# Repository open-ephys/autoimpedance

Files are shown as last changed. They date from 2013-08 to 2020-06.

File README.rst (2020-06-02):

**Warning** This project is deprecated! If you have interest in creating an open source automated electrode plater, please get in touch with us!

=====================
Autoimpedance
=====================

In neuroscience studies, it's important to measure electrode impedances before every experiment. If impedance levels are not in the right range, they must be adjusted by plating electrode tips with gold or platinum. The most common way to do this is with an analog impedance meter and current source, but this method is slow and unreliable. Autoimpedance will be an open-source, digital alternative that aims to speed up the impedance measurement and plating process.

This repository contains code, schematics, and board designs for Autoimpedance. It's based on the Electric Imp and the Analog Devices AD5933_ impedance converter.

Most of the code has been written for Arduino_, but it will soon be translated into Squirrel. PCB layout was done with Eagle_.

What's been done so far
-----------------------------------
- board layout with 32-channel multiplexing capabilities, with the ability to toggle between impedance testing (Analog Devices AD5933) and an adjustable current source (LM234).
- assemble prototype board and verify that multiplexing is working (multiplexing.pde_)
- write code for I2C communication with AD5933 and AD5245 programmable potentiometer (autoimpedance.pde_)

TODO List (short term)
-------------------------------
- calibrate the AD5933 (see instructions in the datasheet_)
- calibrate the LM234 adjustable current source
- create a simple webpage to manually control the device via WiFi
- write and refine a simple feedback algorithm to automatically bring impedance to desired levels
- design and manufacture a case

.. _AD5933: http://www.analog.com/en/rfif-components/direct-digital-synthesis-dds/ad5933/products/product.html
.. _Arduino: http://www.arduino.cc/
.. _Eagle: http://www.cadsoftusa.com/
.. _datasheet: https://github.com/open-ephys/autoimpedance/blob/master/PCB/AD5933.pdf
.. _autoimpedance.pde: https://github.com/open-ephys/autoimpedance/blob/master/autoimpedance.pde
.. _multiplexing.pde: https://github.com/open-ephys/autoimpedance/blob/master/multiplexing.pde

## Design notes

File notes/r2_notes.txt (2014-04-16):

Potential autoimpedance circuit improvements

1. There should be some extra, auxiliary MUX paths tied to various onboard dummy loads (e.g. 10k, 100k, 1M) for gain-factor calibration verification and internal phase measurements (see pgs. 17-19 of AD5933 datasheet).

2. There should be more test points on the circuit.

	> For testing digital pot resistance
	> Power rails
	> I2C bus sockets

3. There should be more information on the silkscreen layers - i.e. component values. 

4. Silk screen font must be larger because print resolution is too course for current size.

X5. Do we need a DC blocking cap at the test_out pin of the AD5933 to prevent the DC bias (table 5 of AD5933 datasheet) on test signal from electroplating during the impedance test?

	> EDIT 1: The DC offset is almost certainly a result of the single supply nature of the ic. The best way to fix this might be to implement a simple virtual ground circuit, and a higher voltage battery to create a negative rail. Then the test signal could be level shifted to 0V. Of course, vgnd would need to drive the saline bath too, so it would have to be a least a little hefty. We could also just send the test signal though an isolator although I doubt Josh will like that approach.
	
	> EDIT 2: The input stage of the AD5933 uses VDD/2 as a reference. Thus, all signals coming out of the device are referenced to this virtual ground, causing them to effectively be bipolar from the perspective of the electrode. Therefore, no DC blocking should be required.

X6. What p2p excitation voltage should we be using?

	> EDIT: Something around 100-200mVPP

X7. Why is the external oscillator required?

	> EDIT: Because the dynamic range with onboard oscillator is 1kHz to 100 kHz, and it is not really accurate in the low end where we need it.

8. There needs to be an off, or at least, reset switch. Sometimes AD5933 becomes unresponsive and requires a power cycle to get back to normal. This could be a programming error, but its good to have a fail-safe.

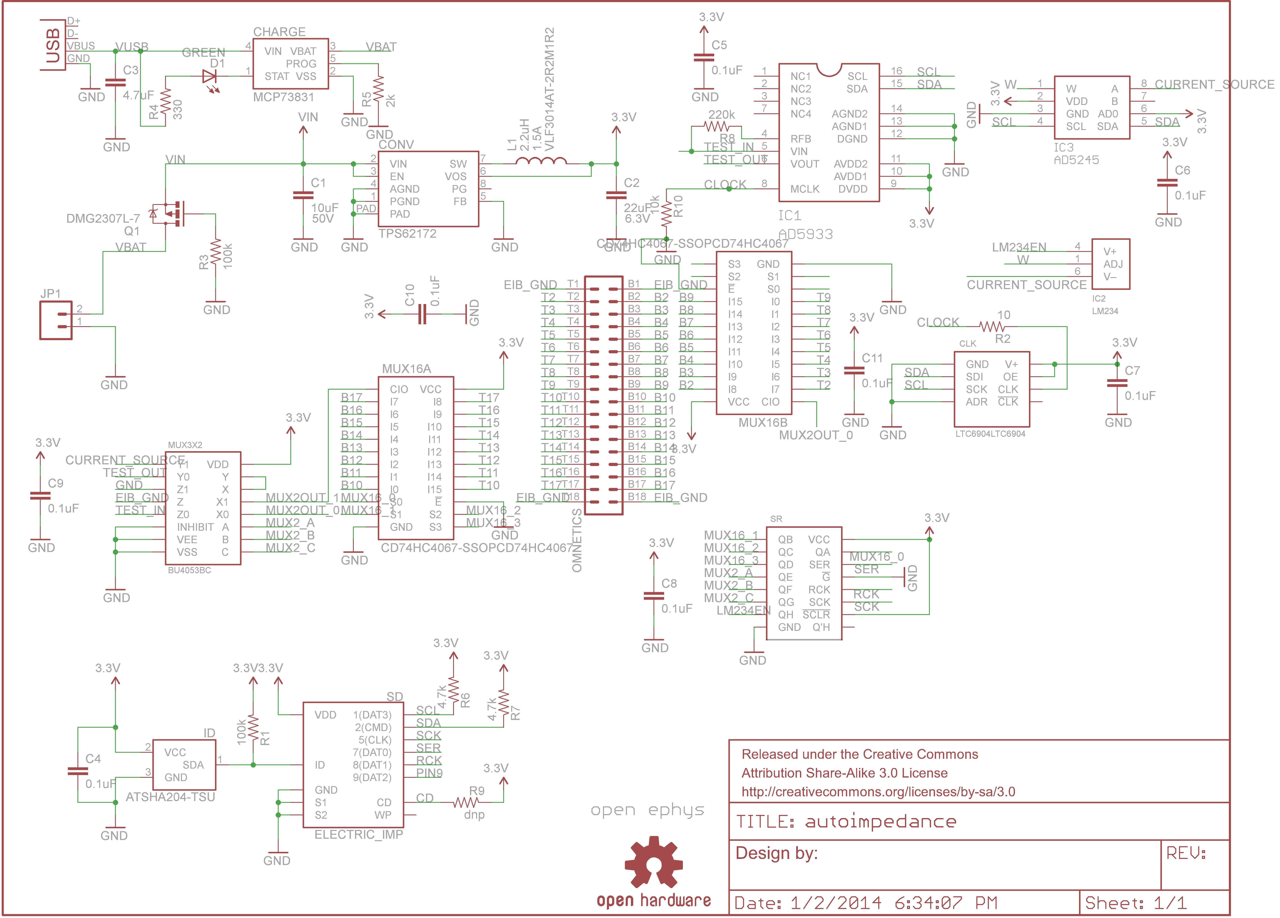
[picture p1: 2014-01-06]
Images/autoimpedance.sch.png

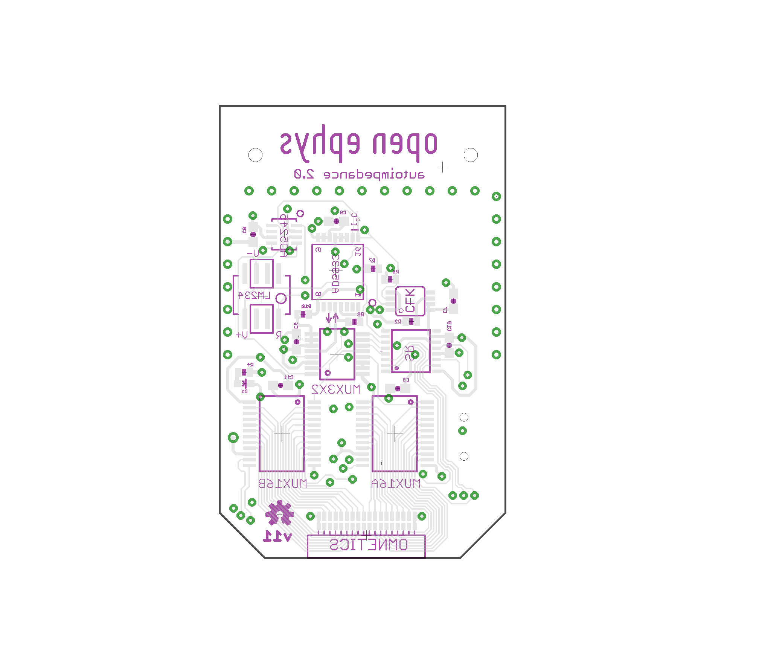
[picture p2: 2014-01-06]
Images/autoimpedance.brd.png

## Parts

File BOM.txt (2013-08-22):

https://docs.google.com/spreadsheet/ccc?key=0An1VoeoG8K6AdDJwWjhla1g5R3o2WVY2MWo2YUxCS2c&usp=sharing

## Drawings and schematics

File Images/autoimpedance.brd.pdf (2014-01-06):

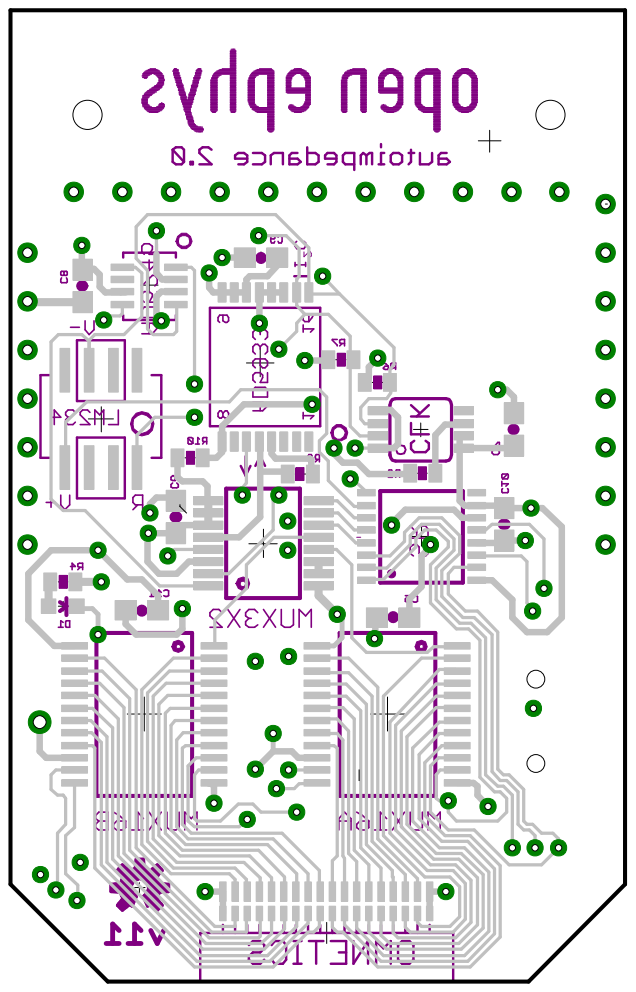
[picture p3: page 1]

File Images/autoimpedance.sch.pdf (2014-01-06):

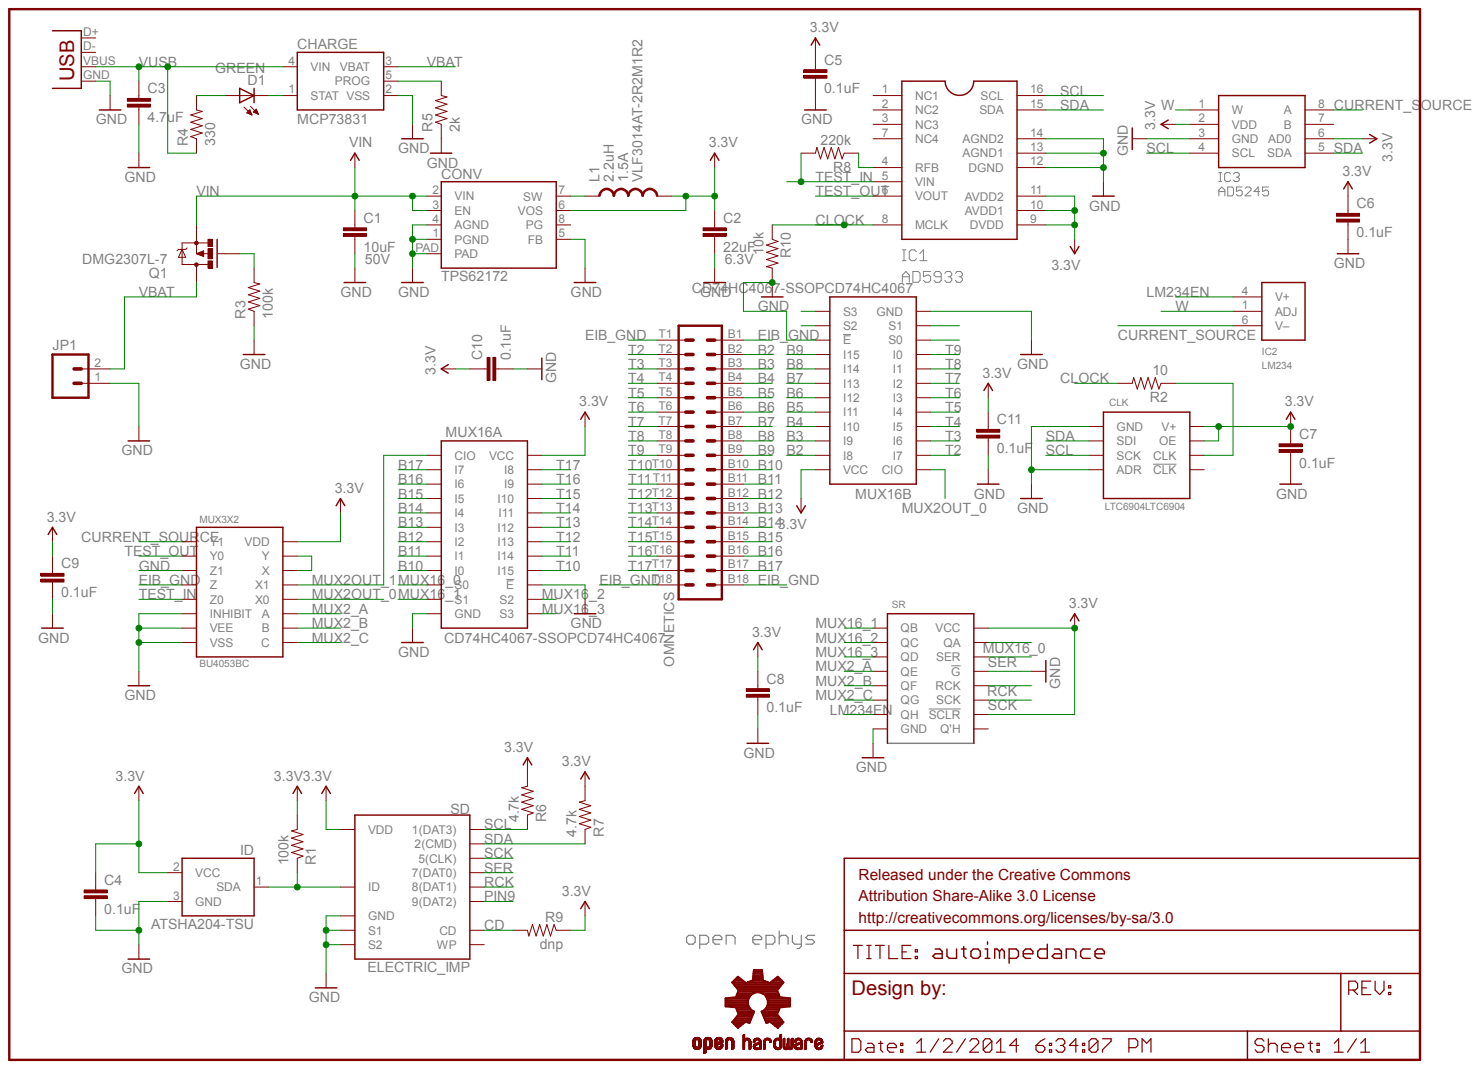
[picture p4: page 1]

GND | | GREEN D1 1

Released under the Creative Commons
Attribution Share-Alike 3.0 License
http://creativecommons.org/licenses/by-sa/3.0

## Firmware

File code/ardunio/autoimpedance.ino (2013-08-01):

// Testing the AD5933

#include <Wire.h>

// The user must calibrate the AD5933 system for a known impedance range to determine the gain factor

#define AD5933_ADDR 0x0D
#define AD5245_ADDR 0x2D //B0101101; // << assumes AD0 tied to VCC

const float CLOCK_SPEED = 16.776*pow(10,6); // AD5933 has internal clock of 16.776 MHz

const int CONTROL_REGISTER[2] =                    { 0x80, 0x81       }; // see mapping below
const int START_FREQUENCY_REGISTER[3] =            { 0x82, 0x83, 0x84 }; // 24 bits for start frequency
const int FREQ_INCREMENT_REGISTER[3] =             { 0x85, 0x86, 0x87 }; // 24 bits for frequency increment
const int NUM_INCREMENTS_REGISTER[2] =             { 0x88, 0x89       }; //  9 bits for # of increments
const int NUM_SETTLING_CYCLES_REGISTER[2] =        { 0x8A, 0x8B       }; //  9 bits + 1 modifier for # of settling times
const int STATUS_REGISTER[1] =                     { 0x8F             }; // see mapping below
const int TEMPERATURE_DATA_REGISTER[2] =	   { 0x92, 0x93       }; // 16-bit, twos complement format
const int REAL_DATA_REGISTER[2] =                  { 0x94, 0x95       }; // 16-bit, twos complement format
const int IMAG_DATA_REGISTER[2] =                  { 0x96, 0x97       }; // 16-bit, twos complement format

// control register map (D15 to D12)
const int DEFAULT_VALUE =                 B0000; // initial setting
const int INITIALIZE =                    B0001; // excite the unknown impedance initially
const int START_SWEEP = 	          B0010; // begin the frequency sweep
const int INCREMENT =                     B0011; // step to the next frequency point
const int REPEAT =                        B0100; // repeat the current frequency point measurement
const int MEASURE_TEMP =                  B1001; // initiates a temperature reading
const int POWER_DOWN =                    B1010; // VOUT and VIN are connected internally to ground
const int STANDBY =                       B1011; // VOUT and VIN are connected internally to ground

const int BLOCK_WRITE = B1010000;
const int BLOCK_READ =  B1010001;
const int ADDRESS_PTR = 0xB0;// B1011000;

const int validTemperatureMeasurement =  1;
const int validImpedanceData =           2;
const int frequencySweepComplete =       4;

const int ledPin = 12;

int reading = 0;
byte rxByte;

// Arduino setup:
// D2 = MUX16A
// D3 = MUX16B
// D4 = MUX16C
// D5 = MUX16D
// D6 = MUX4A
// D7 = MUX4B
// D8 = MUX2A
// D9 = MUX2B
// D10 = LM234 enable
// D11 = buzzer
// D12 = green LED
// D13 = yellow LED

const int mux16A = 2;
const int mux16B = 3;
const int mux16C = 4;
const int mux16D = 5;

const int mux4A = 6;
const int mux4B = 7;

const int mux2A = 8;
const int mux2B = 9;

int channelNumber = 0;

void setup() 
{
  Wire.begin();
  Serial.begin(9600);

  pinMode(ledPin, OUTPUT);
  
  pinMode(mux16A, OUTPUT);
  pinMode(mux16B, OUTPUT);
  pinMode(mux16C, OUTPUT);
  pinMode(mux16D, OUTPUT);
  pinMode(mux4A, OUTPUT);
  pinMode(mux4B, OUTPUT);
  pinMode(mux2A, OUTPUT);
  pinMode(mux2B, OUTPUT);
  
}

void loop() 
{  
  if (Serial.available()) {

    int incomingByte = Serial.read();

    digitalWrite(ledPin, HIGH);

    delay(50);
    
    setSignalPath(0);
    
        configureAD5933(100, // number of settling times
                    1*pow(10,3), // start frequency (Hz)
                    1*pow(10,2), // frequency increment (Hz)
                    30); // number of increments
                    
                     configureAD5245(40*pow(10,3));
    
    for (channelNumber = 0; channelNumber < 1; channelNumber++)
    {
    
      setChannel(channelNumber);

      delay(50);
    
   // measureTemperature();
     
   // delay(50);
     
      measureImpedance();

      digitalWrite(ledPin, LOW);  
    }

  }
}

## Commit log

2012-02-11 Added Eagle files.
    [impedance02.brd, impedance02.sch]
2012-03-30 Moved files into PCB folder
2012-08-31 Moving files around and renaming
    [autoimpedance.brd, autoimpedance.sch]
2013-07-23 Update code for new Arduino software
2013-08-14 Add electric imp board
    [electric-imp-version.brd, electric-imp-version.sch]
2013-08-15 Cleaning up traces
    [electric-imp-version.brd, electric-imp-version.sch]
2013-08-21 Fix layout
    [electric-imp-version.brd, electric-imp-version.sch]
2013-08-22 Aesthetic fixes
    [electric-imp-version.brd, electric-imp-version.sch]
2013-08-22 Fix LM234 channel mapping
    [electric-imp-version.brd, electric-imp-version.sch]
2013-08-22 Update BOM
    [electric-imp-version.brd, electric-imp-version.sch]
2013-08-22 Rename imp version to autoimpedance
    [autoimpedance.brd, autoimpedance.sch, electric-imp-version.brd, electric-imp-version.sch]
2013-08-22 Remove built for imp logo'
    [autoimpedance.brd, autoimpedance.sch]
2013-08-22 Add Gerber files and .cam
    [autoimpedance.brd, autoimpedance.drl, autoimpedance.sch]
2013-09-10 Fix incorrect VEE connection on 3x2 MUX
    [autoimpedance.brd, autoimpedance.sch]
2014-01-06 Switch to i2c89 instead of i2c12
    [autoimpedance.brd, autoimpedance.sch]
2014-04-06 Started transfering autoimpedance code to the electric imp. Verified that i2c bus works in current hardware revision. Developed functions for changing onboard clock frequency. Started an issues list.
2014-04-07 Improved the way that resistances and clock frequency are set.
2014-04-09 Undo changes to old arduino code.
    [autoimpedance.sch]
2014-04-12 Functional base driver with control over all chips on the board. Can perform frequency sweeps, measure impedance, etc. Needs to have calibration arthmetic and methods implemented. Added notes about s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
2014-04-12 Noted a strange bug where the requested current seems to be inversely related to the deliverd current. The pots wiper position is the reflection of where it should be.
2014-04-14 Started implementing calibration routines. I am having trouble with the chip -- it does not seem to want to listen to me when I try to reset sweep parameters.
2014-04-16 Fixed a couple issues with the driver code. The calibration routine is still providing rather strange performance. I need a more systematic way of testing this.
2014-05-08 Added a proper channel mapping doc. There is very strange behavior with the device when trying to run an impedance test. Basically, the data registers are always saturated (contain all 0's or 1's). I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
    [channel-map.xlsx]
